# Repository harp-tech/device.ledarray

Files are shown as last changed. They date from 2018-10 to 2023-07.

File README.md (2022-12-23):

## Harp LED array

Controlling LED arrays that require more power. Ideally for opto-stimulation experiments.

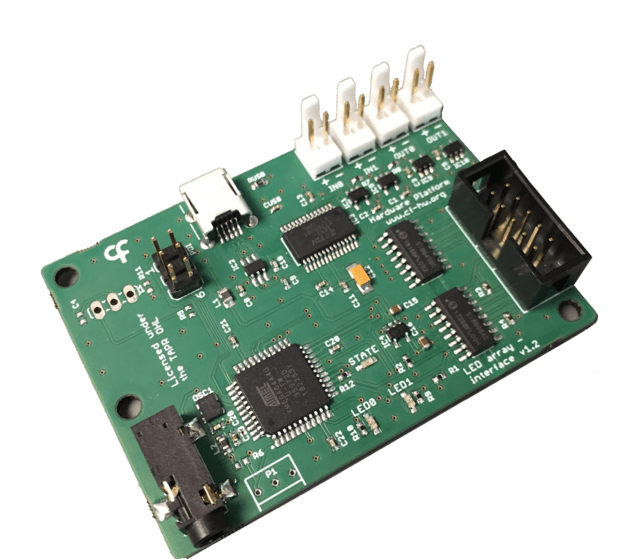
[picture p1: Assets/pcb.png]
harpledarray


### Key Features ###

* Controls up to 2 separate RGB LED
* Arrays and one common Infrared LED
* Two operation modes for each RGB LED Array: PWM or Interval

### Connectivity ###

* 1x clock sync input (CLKIN) [stereo jack]
* 1x USB (for computer) [USB type B]
* 1x flat cable
* 2x Digital Inputs (IN0, IN1) [flick lock male pins]
* 2x Digital Outputs (OUT0, OUT1) [flick lock male pins]
* 1x connector for 2 LED Arrays [10-pin flat-cable]

## Interface ##

The interface with the Harp board can be done through [Bonsai](https://bonsai-rx.org/) or a dedicated GUI (Graphical User Interface).

In order to use this GUI, there are some software that needs to be installed:

1 - Install the [drivers](https://bitbucket.org/fchampalimaud/downloads/downloads/UsbDriver-2.12.26.zip).

2 - Install the [runtime](https://bitbucket.org/fchampalimaud/downloads/downloads/Runtime-1.0.zip).

3 - Reboot the computer.

4 - Install the [GUI](https://bitbucket.org/fchampalimaud/downloads/downloads/Harp%20Led%20Array%20v2.2.0.zip).

## Licensing ##

Each subdirectory will contain a license or, possibly, a set of licenses if it involves both hardware and software.

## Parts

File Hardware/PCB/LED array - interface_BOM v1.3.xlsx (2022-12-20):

Part(s) | Quantity | Description | Distributor | Part. No.
IC1, IC5, IC9, IC10 | 4 | SINGLE BUS BUFFER GATE | Mouser | 595-SN74LVC1G125DBVR
IC2 | 1 | ESD Protection Low Cap | Mouser | 511-USBLC6-2SC6
IC3 | 1 | IC USB USB to Serial UART Enhanced IC SSOP-28 | Mouser | 895-FT232RL
IC4 | 1 | LP5907MFX-3.3/NOPB LDO 3.3Vout, 250mA | Mouser | 595-LP5907MFX-3.3NPB
IC6 | 1 | ATXMEGA64A4U-AU, ATxmega, 32 MHz, 64 KB, 4 KB, 44, TQFP | Mouser | 556-ATXMEGA64A4U-AU
IC7 | 1 | Isolator Si8645BC-B-IS1 | Mouser | 634-SI8645BC-B-IS1
IC8 | 1 | Isolator SI8606AC-B-IS1 | Mouser | 634-SI8606AC-B-IS1
L1 | 1 | MI0805K400R-10 FERRITE, BEAD, 2012, 100MHZ, 40R | Mouser | 875-MI0805K400R-10
L2 | 1 | FERRITE BEAD, 0.07OHM, 1.5A, 0603 | Mouser | 81-BLM18SG331TN1D
R9, R10, R12 | 3 | RES SMD 0402 68Ω, ± 5% | Mouser | 667-ERJ-2GEJ680X
R6 | 0 | RES SMD 0402 1kΩ, ± 0.1% | Farnell | 1697320
R1, R2, R3, R4 | 4 | RES SMD 0402 3kΩ, ± 1% | Mouser | 667-ERJ-2RKF3001X
R7, R8 | 2 | RES SMD 0402 100kΩ, ± 1% | REEL | REEL
RUSB | 1 | RES SMD 1MΩ 1/4W 5% 75V 0603 | Mouser | 71-CRCW06031M00JNEAH
C9, C10 | 2 | CAP CER 47pF 50V C0G 5% 0402 | Mouser | 81-GCM1555C1H470JA6D
CUSB | 1 | CAP CER 4.7nF 50 V ± 10% 0402 | Mouser | 710-885012205048
C1, C2, C3, C5, C8, C11, C13, C14, C20, C21, C22, C28 | 11 | CAP CER 100nF 10V X5R 0402 | REEL | REEL
C23 | 1 | CAP CER 0.33uF 16V 10% X72 0402 | Mouser | 810-CGA2B1X7S1C334KC
C15, C16 | 2 | CAP CER 4.7uF 35V X5R 10% 0603 | Mouser | 81-GRM188R6YA475KE5D
C12 | 1 | CAP TAN 4.7uF 10V 10% | Mouser | 80-T494A475M010
LED0, LED1, STATE | 3 | LED, Green, 1.6mm x 0.8mm, 566 nm, 2.1 V, 20 mA, 15 mcd | Mouser | 78-TLMP1100-GS08
P1 | 0 | SQ 500 OHM 10% 0.5WATTS | Mouser | 652-3362M-1-501LF
JP1 | 1 | 10 Contacts, Header, 2.54 mm, Through Hole, 2 Rows | Mouser | 517-30310-6002
USB | 1 | USB MINI B RECEPT RA TH W/POST | Mouser | 798-UX60-MB-5S8
USB Cable | 1 | USB A - MINI-B 0.8M - MINI-B 0.8M BLACK | Mouser | 538-88732-8502
OSC1 | 1 | 32MHz 10ppm | Mouser | 998-1001CI5032.0000T
CLKIN | 1 | SMT 3.5 STEREO REEL | Mouser | 502-35RASMT2BHNTRX
PDI | 1 | CONN HEADER 6POS .100 STR | Mouser | 649-67996-206HLF
IN0, IN1, OUT0, OUT1 | 4 | Vertical, KK 6410 Series, 2 Contacts, Header, 2.54 mm | Mouser | 538-22-29-2021
SV1 | 0 | 3POS Gold Male | Mouser | 649-68001-203HLF
Components | 53
Licensed under the TAPR Open Hardware License (www.tapr.org/OHL)
Copyright 2018 Artur Silva and Filipe Carvalho

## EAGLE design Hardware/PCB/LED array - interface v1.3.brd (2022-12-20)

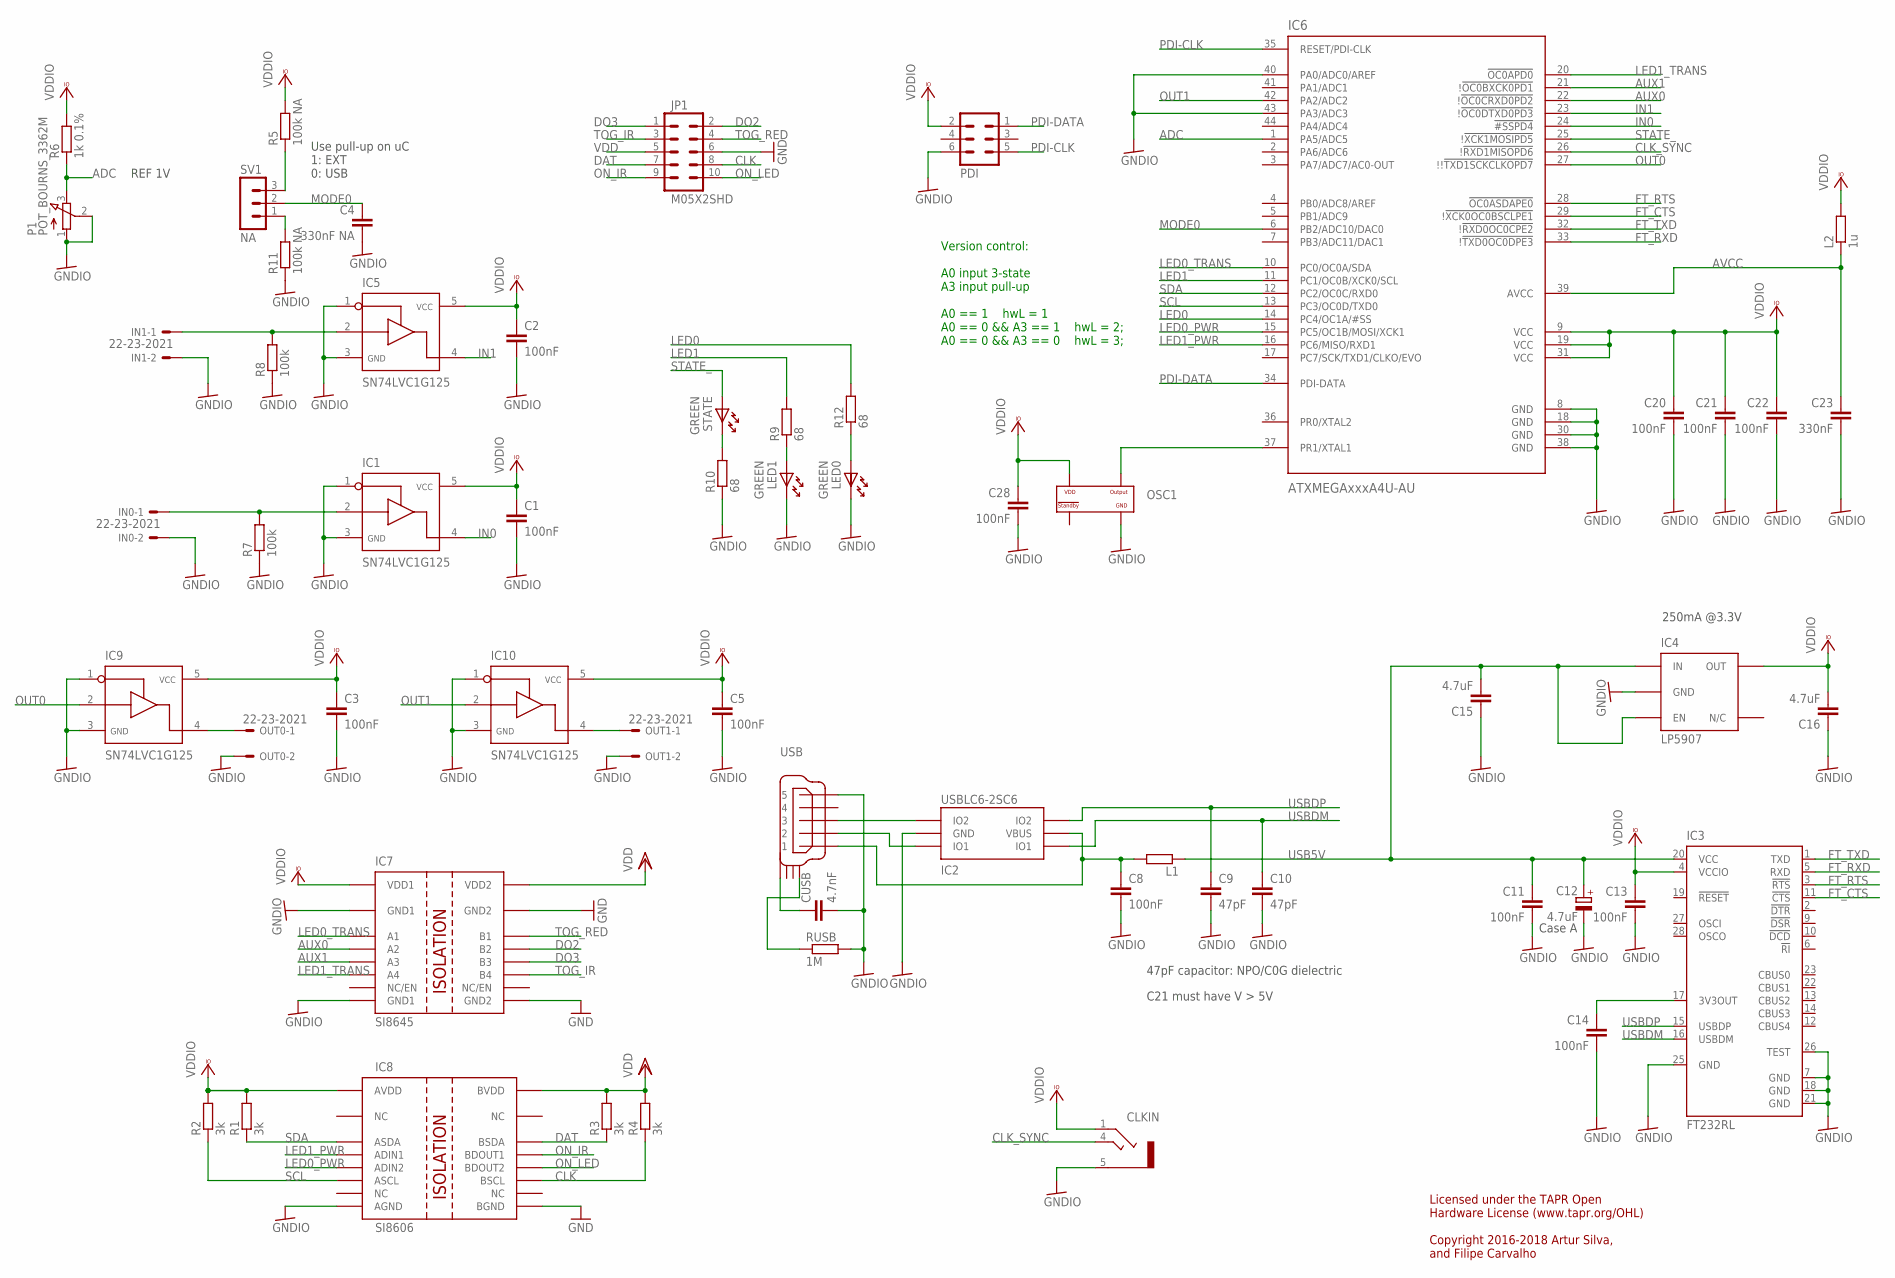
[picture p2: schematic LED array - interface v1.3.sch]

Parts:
C1, C2, C3, C5, C8, C11, C13, C14, C20, C21, C22, C28: 100nF; C0402
C4: 330nF NA; C0402
C9, C10: 47pF; C0402
C12: 4.7uF; A/3216-18W
C15, C16: 4.7uF; C0402
C23: 330nF; C0402
CLKIN: STEREO_JACK; 35RASMT2BHNTRX
CUSB: 4.7nF; C0402
IC1, IC5, IC9, IC10: SN74LVC1G125; SOT23-5
IC2: USBLC6-2SC6; SOT23-6L
IC3: FT232RL; SSOP28
IC4: LP5907; TSOT23-5
IC6: ATXMEGAxxxA4U-AU; QFP80P1200X1200X120-44N
IC7: SI8645; NSOIC-16
IC8: SI8606; NSOIC-16
IN0, IN1: 22-23-2021
JP1: M05X2SHD; 2X5-SHROUDED
L1: ???; R0805
L2: 1u; R0805
LED0, LED1: GREEN; LED_HAND
OSC1: OSCILLATOR; OSCILLATOR_3.2X2.5
OUT0, OUT1: 22-23-2021
P1: POT_BOURNS_3362M
PDI: MA03-2
R1, R2, R3, R4: 3k; R0402
R5, R11: 100k NA; R0402
R6: 1k 0.1%; R0402
R7, R8: 100k; R0402
R9, R10, R12: 68; R0402
RUSB: 1M; R0603
STATE: GREEN; LED_HAND
SV1: NA; MA03-1
USB: USB_MINI_B; 240-0002-1

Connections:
ADC: IC6.1 (PA5/ADC5), P1.3 (E), R6.1
ADC1: R5.1, SV1.3
AUX0: IC6.22 (!!OC0CRXD0PD2), IC7.4 (A2)
AUX1: IC6.21 (!!OC0BXCK0PD1), IC7.5 (A3)
AVCC: C23.1, IC6.39 (AVCC), L2.1
CLK: IC8.11 (BSCL), JP1.8, R4.1
CLK_SYNC: CLKIN.4, IC6.26 (!!RXD1MISOPD6)
DAT: IC8.14 (BSDA), JP1.7, R3.1
DO2: IC7.13 (B2), JP1.2
DO3: IC7.12 (B3), JP1.1
FT_CTS: IC3.11 (!CTS), IC6.29 (!!XCK0OC0BSCLPE1)
FT_RTS: IC3.3 (!RTS), IC6.28 (!OC0ASDAPE0)
FT_RXD: IC3.5 (RXD), IC6.33 (!!TXD0OC0DPE3)
FT_TXD: IC3.1 (TXD), IC6.32 (!!RXD0OC0CPE2)
GND: IC7.9 (GND2), IC7.15 (GND2), IC8.9 (BGND), JP1.6
GND2: IC5.2, IN1.1, R8.2
GNDIO: C1.2, C2.2, C3.2, C4.2, C5.2, C8.2, C9.2, C10.2, C11.2, C12.-, C13.2, C14.2, C15.1, C16.1, C20.2, C21.2, C22.2, C23.2, C28.2, CLKIN.5, CUSB.2, IC1.1, IC1.3, IC2.P$2 (GND), IC3.7 (GND), IC3.18 (GND), IC3.21 (GND), IC3.25 (GND), IC3.26 (TEST), IC4.2 (GND), IC5.1, IC5.3, IC6.8 (GND), IC6.18 (GND), IC6.30 (GND), IC6.38 (GND), IC6.40 (PA0/ADC0/AREF), IC6.43 (PA3/ADC3), IC7.2 (GND1), IC7.8 (GND1), IC8.8 (AGND), IC9.1, IC9.3, IC10.1, IC10.3, IN0.2, IN1.2, LED0.K, LED1.K, OSC1.P$2 (GND), OUT0.2, OUT1.2, P1.1 (A), P1.2 (S), PDI.6, R7.1, R8.1, R10.1, R11.1, RUSB.2, USB.P$5 (5)
IN0: IC1.4, IC6.24 (!#SSPD4)
IN1: IC5.4, IC6.23 (!!OC0DTXD0PD3)
LED0: IC6.14 (PC4/OC1A/#SS), R12.2
LED0_PWR: IC6.15 (PC5/OC1B/MOSI/XCK1), IC8.5 (ADIN2)
LED0_TRANS: IC6.10 (PC0/OC0A/SDA), IC7.3 (A1)
LED1: IC6.11 (PC1/OC0B/XCK0/SCL), R9.2
LED1_PWR: IC6.16 (PC6/MISO/RXD1), IC8.4 (ADIN1)
LED1_TRANS: IC6.20 (!OC0APD0), IC7.6 (A4)
MODE0: C4.1, IC6.6 (PB2/ADC10/DAC0), SV1.2
unnamed: R11.2, SV1.1
unnamed: C14.1, IC3.17 (3V3OUT)
unnamed: IC9.4, OUT0.1
unnamed: IC2.P$3 (IO2), USB.P$3 (3)
unnamed: LED0.A, R12.1
unnamed: IC10.4, OUT1.1
unnamed: R10.2, STATE.K
unnamed: IC1.2, IN0.1, R7.2
unnamed: LED1.A, R9.1
unnamed: C8.1, IC2.P$5 (VBUS), L1.2, USB.P$1 (1)
unnamed: IC2.P$1 (IO1), USB.P$2 (2)
unnamed: CUSB.1, USB.SHIELD_4
unnamed: RUSB.1, USB.SHIELD_1
ON_IR: IC8.13 (BDOUT1), JP1.9
ON_LED: IC8.12 (BDOUT2), JP1.10
OSC1: IC6.37 (PR1/XTAL1), OSC1.P$3 (OUTPUT)
OUT0: IC6.27 (!!!TXD1SCKCLKOPD7), IC9.2
OUT1: IC6.42 (PA2/ADC2), IC10.2
PDI-CLK: IC6.35 (RESET/PDI-CLK), PDI.5
PDI-DATA: IC6.34 (PDI-DATA), PDI.1
SCL: IC6.13 (PC3/OC0D/TXD0), IC8.6 (ASCL), R2.1
SDA: IC6.12 (PC2/OC0C/RXD0), IC8.3 (ASDA), R1.1
STATE_: IC6.25 (!!XCK1MOSIPD5), STATE.A
TOG_IR: IC7.11 (B4), JP1.3
TOG_RED: IC7.14 (B1), JP1.4
USB5V: C11.1, C12.+, C15.2, IC3.20 (VCC), IC4.1 (IN), IC4.3 (EN), L1.1
USBDM: C10.1, IC2.P$6 (IO1), IC3.16 (USBDM)
USBDP: C9.1, IC2.P$4 (IO2), IC3.15 (USBDP)
VCCIO: C1.1, C2.1, C3.1, C5.1, C13.1, C16.2, C20.1, C21.1, C22.1, C28.1, CLKIN.1, IC1.5, IC3.4 (VCCIO), IC4.5 (OUT), IC5.5, IC6.9 (VCC), IC6.19 (VCC), IC6.31 (VCC), IC7.1 (VDD1), IC8.1 (AVDD), IC9.5, IC10.5, L2.2, OSC1.P$4 (VDD), PDI.2, R1.2, R2.2, R5.2, R6.2
VDD: IC7.16 (VDD2), IC8.16 (BVDD), JP1.5, R3.2, R4.2

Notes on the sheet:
250mA @3.3V
Case A
47pF capacitor: NPO/C0G dielectric
C21 must have V > 5V
Use pull-up on uC 1: EXT 0: USB
REF 1V
Licensed under the TAPR Open Hardware License (www.tapr.org/OHL) Copyright 2016-2018 Artur Silva, and Filipe Carvalho
Version control: A0 input 3-state A3 input pull-up A0 == 1 hwL = 1 A0 == 0 && A3 == 1 hwL = 2; A0 == 0 && A3 == 0 hwL = 3;

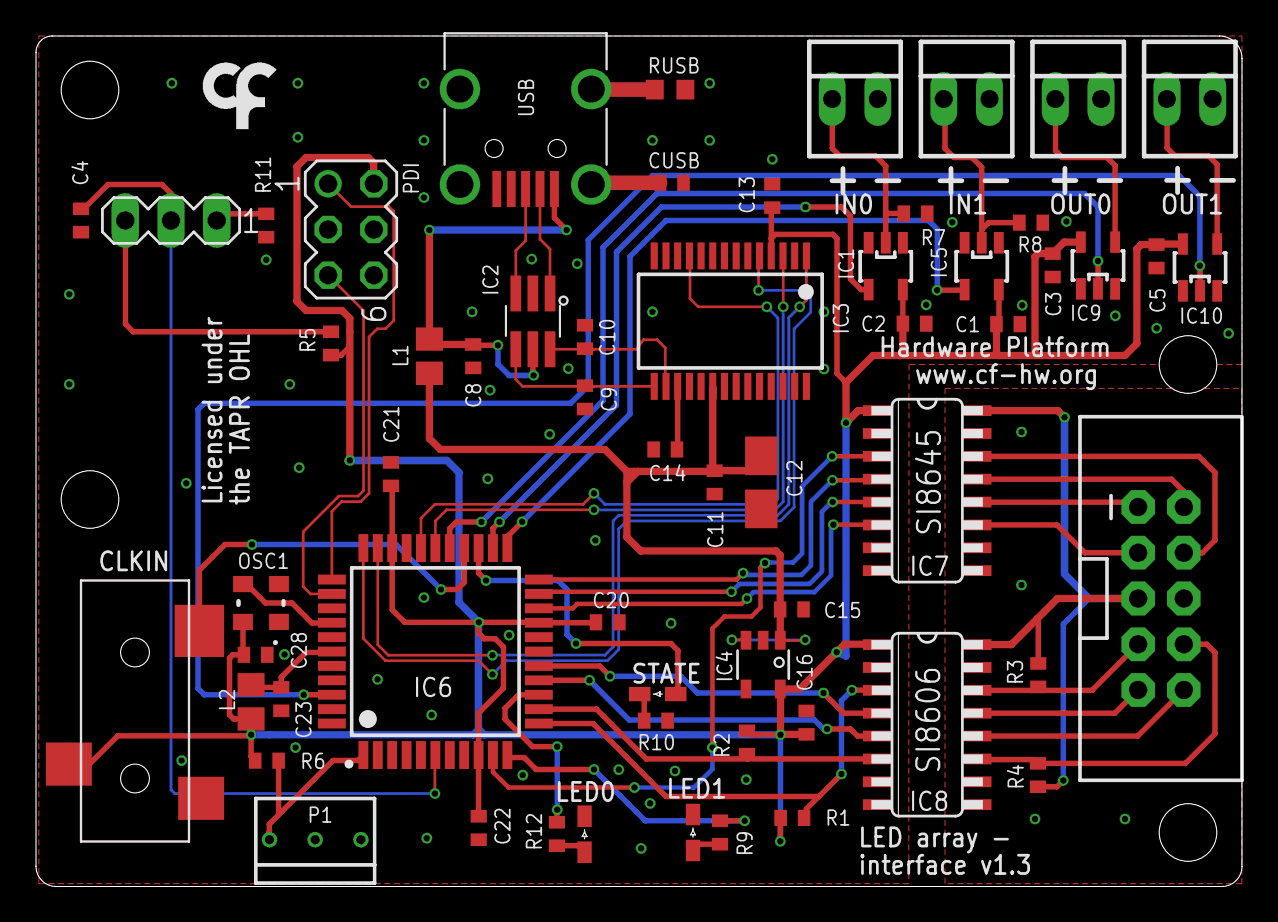
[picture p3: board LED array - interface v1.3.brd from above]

Board: 2 copper layers, 67.0 x 47.2 mm, 61 parts (1 on the bottom side), 56 nets.

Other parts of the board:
U$1: LOGO_5
U$3: LOGO_7

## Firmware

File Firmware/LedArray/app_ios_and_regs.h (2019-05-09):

#ifndef _APP_IOS_AND_REGS_H_
#define _APP_IOS_AND_REGS_H_
#include "cpu.h"

void init_ios(void);
/************************************************************************/
/* Definition of input pins                                             */
/************************************************************************/
// VERSION0               Description: Check hardware version
// VERSION1               Description: Check hardware version
// IN0                    Description: Board's input IN0
// IN1                    Description: Board's input IN1

#define read_VERSION0 read_io(PORTA, 0)         // VERSION0
#define read_VERSION1 read_io(PORTA, 3)         // VERSION1
#define read_IN0 read_io(PORTD, 4)              // IN0
#define read_IN1 read_io(PORTD, 3)              // IN1

/************************************************************************/
/* Definition of output pins                                            */
/************************************************************************/
// LED0_TRANSISTOR        Description: Controls transistor of LED0
// BOARD_LED1             Description: Board's LED1
// LED0_PWR_ON            Description: Enables power for LED0
// LED1_PWR_ON            Description: Enables power for LED1
// LED1_TRANSISTOR        Description: Controls transistor of LED1
// AUX1                   Description: Dummy digital output
// AUX0                   Description: Dummy digital output
// BOARD_LED0             Description: Board's LED0
// OUT0                   Description: Board's output OUT1
// OUT1                   Description: Board's output OUT0

/* LED0_TRANSISTOR */
#define set_LED0_TRANSISTOR set_io(PORTC, 0)
#define clr_LED0_TRANSISTOR clear_io(PORTC, 0)
#define tgl_LED0_TRANSISTOR toggle_io(PORTC, 0)
#define read_LED0_TRANSISTOR read_io(PORTC, 0)

/* BOARD_LED1 */
#define set_BOARD_LED1 set_io(PORTC, 1)
#define clr_BOARD_LED1 clear_io(PORTC, 1)
#define tgl_BOARD_LED1 toggle_io(PORTC, 1)
#define read_BOARD_LED1 read_io(PORTC, 1)

/* LED0_PWR_ON */
#define set_LED0_PWR_ON set_io(PORTC, 5)
#define clr_LED0_PWR_ON clear_io(PORTC, 5)
#define tgl_LED0_PWR_ON toggle_io(PORTC, 5)
#define read_LED0_PWR_ON read_io(PORTC, 5)

/* LED1_PWR_ON */
#define set_LED1_PWR_ON set_io(PORTC, 6)
#define clr_LED1_PWR_ON clear_io(PORTC, 6)
#define tgl_LED1_PWR_ON toggle_io(PORTC, 6)
#define read_LED1_PWR_ON read_io(PORTC, 6)

/* LED1_TRANSISTOR */
#define set_LED1_TRANSISTOR set_io(PORTD, 0)
#define clr_LED1_TRANSISTOR clear_io(PORTD, 0)
#define tgl_LED1_TRANSISTOR toggle_io(PORTD, 0)
#define read_LED1_TRANSISTOR read_io(PORTD, 0)

/* AUX1 */
#define set_AUX1 set_io(PORTD, 1)
#define clr_AUX1 clear_io(PORTD, 1)
#define tgl_AUX1 toggle_io(PORTD, 1)
#define read_AUX1 read_io(PORTD, 1)

/* AUX0 */
#define set_AUX0 set_io(PORTD, 2)
#define clr_AUX0 clear_io(PORTD, 2)
#define tgl_AUX0 toggle_io(PORTD, 2)
#define read_AUX0 read_io(PORTD, 2)

/* BOARD_LED0 */
#define set_BOARD_LED0 set_io(PORTC, 4)
#define clr_BOARD_LED0 clear_io(PORTC, 4)
#define tgl_BOARD_LED0 toggle_io(PORTC, 4)
#define read_BOARD_LED0 read_io(PORTC, 4)

/* OUT0 */
#define set_OUT0 set_io(PORTD, 7)
#define clr_OUT0 clear_io(PORTD, 7)
#define tgl_OUT0 toggle_io(PORTD, 7)
#define read_OUT0 read_io(PORTD, 7)

/* OUT1 */
#define set_OUT1 set_io(PORTA, 2)
#define clr_OUT1 clear_io(PORTA, 2)
#define tgl_OUT1 toggle_io(PORTA, 2)
#define read_OUT1 read_io(PORTA, 2)


/************************************************************************/
/* Registers' structure                                                 */
/************************************************************************/
typedef struct
{
	uint8_t REG_POWER_EN;
	uint8_t REG_LED_BEHAVING;
	uint8_t REG_LED_ON;
	uint8_t REG_IN_STATE;
	uint8_t REG_OUT_CONFIGURATION;
	uint8_t REG_IN_CONFIGURATION;
	uint8_t REG_LED_CONFIGURATION;
	uint8_t REG_LED0_SUPPLY_PWR_CONF;
	uint8_t REG_LED1_SUPPLY_PWR_CONF;
	float REG_LED0_PWM_FREQ;
	float REG_LED0_PWM_DCYCLE;
	uint16_t REG_LED0_PWM_PULSES;
	uint16_t REG_LED0_INTERVAL_ON;
	uint16_t REG_LED0_INTERVAL_OFF;
	uint16_t REG_LED0_INTERVAL_PULSES;
	uint16_t REG_LED0_INTERVAL_TAIL;
	uint16_t REG_LED0_INTERVAL_REPS;
	float REG_LED1_PWM_FREQ;
	float REG_LED1_PWM_DCYCLE;
	uint16_t REG_LED1_PWM_PULSES;
	uint16_t REG_LED1_INTERVAL_ON;
	uint16_t REG_LED1_INTERVAL_OFF;
	uint16_t REG_LED1_INTERVAL_PULSES;
	uint16_t REG_LED1_INTERVAL_TAIL;
	uint16_t REG_LED1_INTERVAL_REPS;
	float REG_LED0_PWM_FREQ_REAL;
	float REG_LED0_PWM_DCYCLE_REAL;
	float REG_LED1_PWM_FREQ_REAL;
	float REG_LED1_PWM_DCYCLE_REAL;
	uint8_t REG_AUX_DIG_OUT;
	uint8_t REG_AUX_SUPPLY_PWR_CONF;
	uint8_t REG_OUT_STATE;
	uint8_t REG_DUMMY0;
	uint8_t REG_EVNT_ENABLE;
} AppRegs;

/************************************************************************/
/* Registers' address                                                   */
/************************************************************************/
/* Registers */
#define ADD_REG_POWER_EN                    32 // U8     Control the enable of both LEDs' supply
#define ADD_REG_LED_BEHAVING                33 // U8     Starts and stops the LED is behaving
#define ADD_REG_LED_ON                      34 // U8     Controls the on board's LED
#define ADD_REG_IN_STATE                    35 // U8     Reflects the state of both inputs
#define ADD_REG_OUT_CONFIGURATION           36 // U8     Configures which signal is connected to the digital outputs
#define ADD_REG_IN_CONFIGURATION            37 // U8     Configures the digital inputs
#define ADD_REG_LED_CONFIGURATION           38 // U8     Configures how LEDs will behave
#define ADD_REG_LED0_SUPPLY_PWR_CONF        39 // U8     Configuration of power to be aplied to LED0 [1;120]
#define ADD_REG_LED1_SUPPLY_PWR_CONF        40 // U8     Configuration of power to be aplied to LED1 [1;120]
#define ADD_REG_LED0_PWM_FREQ               41 // FLOAT  PWM frequency of LED0's power transistor [0.5;2000.0]
#define ADD_REG_LED0_PWM_DCYCLE             42 // FLOAT  PWM duty cycle of LED0's power transistor [0.1;99.9]
#define ADD_REG_LED0_PWM_PULSES             43 // U16    Number of PWM pulses (LED0) [1;65535]
#define ADD_REG_LED0_INTERVAL_ON            44 // U16    Time ON of LED0 (milliseconds) [1;65535]
#define ADD_REG_LED0_INTERVAL_OFF           45 // U16    Time OFF of LED0 (milliseconds) [1;65535]
#define ADD_REG_LED0_INTERVAL_PULSES        46 // U16    Number of pulses (LED0) [1;65535]
#define ADD_REG_LED0_INTERVAL_TAIL          47 // U16    Wait time between pulses (milliseconds) (LED0) [1;65535]
#define ADD_REG_LED0_INTERVAL_REPS          48 // U16    Number of repetitions of the entire scheme (LED0) [1;65535]
#define ADD_REG_LED1_PWM_FREQ               49 // FLOAT  PWM frequency of LED1's power transistor [0.5;2000.0]
#define ADD_REG_LED1_PWM_DCYCLE             50 // FLOAT  PWM duty cycle of LED1's power transistor [0.1;99.9]
#define ADD_REG_LED1_PWM_PULSES             51 // U16    Number of PWM pulses (LED1) [1;65535]
#define ADD_REG_LED1_INTERVAL_ON            52 // U16    Time ON of LED1 (milliseconds) [1;65535]
#define ADD_REG_LED1_INTERVAL_OFF           53 // U16    Time OFF of LED1 (milliseconds) [1;65535]
#define ADD_REG_LED1_INTERVAL_PULSES        54 // U16    Number of pulses (LED1) [1;65535]
#define ADD_REG_LED1_INTERVAL_TAIL          55 // U16    Wait time between pulses (milliseconds) (LED1) [1;65535]
#define ADD_REG_LED1_INTERVAL_REPS          56 // U16    Number of repetitions of the entire scheme (LED1) [1;65535]
#define ADD_REG_LED0_PWM_FREQ_REAL          57 // FLOAT  Real PWM frequency of LED0's power transistor
#define ADD_REG_LED0_PWM_DCYCLE_REAL        58 // FLOAT  Real PWM duty cycle of LED0's power transistor
#define ADD_REG_LED1_PWM_FREQ_REAL          59 // FLOAT  Real PWM frequency of LED1's power transistor
#define ADD_REG_LED1_PWM_DCYCLE_REAL        60 // FLOAT  Real PWM duty cycle of LED1's power transistor
#define ADD_REG_AUX_DIG_OUT                 61 // U8     Controls the auxiliar digital output
#define ADD_REG_AUX_SUPPLY_PWR_CONF         62 // U8     Configuration of power to be aplied to auxiliar LED [1;120]
#define ADD_REG_OUT_STATE                   63 // U8     Digital output control
#define ADD_REG_DUMMY0                      64 // U8     Not used
#define ADD_REG_EVNT_ENABLE                 65 // U8     Enable the Events

/************************************************************************/
/* PWM Generator registers' memory limits                               */
/*                                                                      */
/* DON'T change the APP_REGS_ADD_MIN value !!!                          */
/* DON'T change these names !!!                                         */
/************************************************************************/
/* Memory limits */
#define APP_REGS_ADD_MIN                    0x20
#define APP_REGS_ADD_MAX                    0x41
#define APP_NBYTES_OF_REG_BANK              70
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

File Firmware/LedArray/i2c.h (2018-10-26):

#ifndef _I2C_H_
#define _I2C_H_

#include "i2c_user.h"


//*****************************************************************************
// If not defined, define bool, true and false
//*****************************************************************************
#ifndef bool
	#define bool uint8_t
#endif
#ifndef true
	#define true 1
#endif
#ifndef false
	#define false 0
#endif

//*****************************************************************************
// Define I2C structure for the devices
//*****************************************************************************
#ifndef MAX_I2C_DATA
	#define MAX_I2C_DATA 32
#endif

typedef struct {
	unsigned char add;
	unsigned char reg;
	unsigned char reg_val;
	unsigned char data[MAX_I2C_DATA];
} i2c_dev_t;


//*****************************************************************************
// Check if any of the four I2C buses is used
//*****************************************************************************
#ifdef I2C0_CLK
	#ifndef I2C0_PORT
		#error "Bus I2C0 is enabled but I2C0_PORT is not defined"
	#endif
	#ifndef I2C0_SDA
		#error "Bus I2C0 is enabled but I2C0_SDA is not defined"
	#endif
	#ifndef I2C0_SCL
		#error "Bus I2C0 is enabled but I2C0_SCL is not defined"
	#endif
	#ifndef F_CPU
		#error "Bus I2C0 is enabled but F_CPU is not defined"
	#endif
	#if   F_CPU == 32000000
	#elif F_CPU == 16000000
	#elif F_CPU ==  8000000
	#elif F_CPU ==  4000000
	#elif F_CPU ==  2000000
	#elif F_CPU ==  1000000
	#else
	#error "I2C0: Unsupported F_CPU value for system clock"
	#endif
#endif

#ifdef I2C1_CLK
	#ifndef I2C1_PORT
		#error "Bus I2C1 is enabled but I2C1_PORT is not defined"
	#endif
	#ifndef I2C1_SDA
		#error "Bus I2C1 is enabled but I2C1_SDA is not defined"
	#endif
	#ifndef I2C1_SCL
		#error "Bus I2C1 is enabled but I2C1_SCL is not defined"
	#endif
	#ifndef F_CPU
		#error "Bus I2C1 is enabled but F_CPU is not defined"
	#endif
	#if   F_CPU == 32000000
	#elif F_CPU == 16000000
	#elif F_CPU ==  8000000
	#elif F_CPU ==  4000000
	#elif F_CPU ==  2000000
	#elif F_CPU ==  1000000
	#else
	#error "I2C1: Unsupported F_CPU value for system clock"
	#endif
#endif

#ifdef I2C2_CLK
	#ifndef I2C2_PORT
		#error "Bus I2C2 is enabled but I2C2_PORT is not defined"
	#endif
	#ifndef I2C2_SDA
		#error "Bus I2C2 is enabled but I2C2_SDA is not defined"
	#endif
	#ifndef I2C2_SCL
		#error "Bus I2C2 is enabled but I2C2_SCL is not defined"
	#endif
	#ifndef F_CPU
		#error "Bus I2C2 is enabled but F_CPU is not defined"
	#endif
	#if   F_CPU == 32000000
	#elif F_CPU == 16000000
	#elif F_CPU ==  8000000
	#elif F_CPU ==  4000000
	#elif F_CPU ==  2000000
	#elif F_CPU ==  1000000
	#else
	#error "I2C2: Unsupported F_CPU value for system clock"
	#endif
#endif

#ifdef I2C3_CLK
	#ifndef I2C3_PORT
		#error "Bus I2C3 is enabled but I2C3_PORT is not defined"
	#endif
	#ifndef I2C3_SDA
		#error "Bus I2C3 is enabled but I2C3_SDA is not defined"
	#endif
	#ifndef I2C3_SCL
		#error "Bus I2C3 is enabled but I2C3_SCL is not defined"
	#endif
	#ifndef F_CPU
		#error "Bus I2C3 is enabled but F_CPU is not defined"
	#endif
	#if   F_CPU == 32000000
	#elif F_CPU == 16000000
	#elif F_CPU ==  8000000
	#elif F_CPU ==  4000000
	#elif F_CPU ==  2000000
	#elif F_CPU ==  1000000
	#else
	#error "I2C3: Unsupported F_CPU value for system clock"
	#endif
#endif



//*****************************************************************************
// Define SCL delays
//*****************************************************************************
#ifdef I2C0_CLK
	#define tCLK_I2C0 I2C0_CLK
#endif
#ifdef I2C1_CLK
	#define tCLK_I2C1 I2C1_CLK
#endif
#ifdef I2C2_CLK
	#define tCLK_I2C2 I2C2_CLK
#endif
#ifdef I2C3_CLK
	#define tCLK_I2C3 I2C3_CLK
#endif

//*****************************************************************************
// Define IOs interface
//*****************************************************************************
#ifdef I2C0_CLK
	#define set_SDA0 set_io(I2C0_PORT, I2C0_SDA)
	#define clear_SDA0 clear_io(I2C0_PORT, I2C0_SDA)
	#define toggle_SDA0 toggle_io(I2C0_PORT, I2C0_SDA)
	#define set_SCL0 set_io(I2C0_PORT, I2C0_SCL)
	#define clear_SCL0 clear_io(I2C0_PORT, I2C0_SCL)
	#define toggle_SCL0 toggle_io(I2C0_PORT, I2C0_SCL)
	#define read_SDA0 read_io(I2C0_PORT, I2C0_SDA)
	#define set_SDA0_and_SCL0 set_io_mask(I2C0_PORT, (1<<I2C0_SDA) | (1<<I2C0_SCL))
	#define clear_SDA0_and_SCL0 clear_io_mask(I2C0_PORT, (1<<I2C0_SDA) | (1<<I2C0_SCL))
#endif

#ifdef I2C1_CLK
	#define set_SDA1 set_io(I2C1_PORT, I2C1_SDA)
	#define clear_SDA1 clear_io(I2C1_PORT, I2C1_SDA)
	#define toggle_SDA1 toggle_io(I2C1_PORT, I2C1_SDA)
	#define set_SCL1 set_io(I2C1_PORT, I2C1_SCL)
	#define clear_SCL1 clear_io(I2C1_PORT, I2C1_SCL)
	#define toggle_SCL1 toggle_io(I2C1_PORT, I2C1_SCL)
	#define read_SDA1 read_io(I2C1_PORT, I2C1_SDA)
	#define set_SDA1_and_SCL1 set_io_mask(I2C1_PORT, (1<<I2C1_SDA) | (1<<I2C1_SCL))
	#define clear_SDA1_and_SCL1 clear_io_mask(I2C1_PORT, (1<<I2C1_SDA) | (1<<I2C1_SCL))
#endif

#ifdef I2C2_CLK
	#define set_SDA2 set_io(I2C2_PORT, I2C2_SDA)
	#define clear_SDA2 clear_io(I2C2_PORT, I2C2_SDA)
	#define toggle_SDA2 toogle_io(I2C2_PORT, I2C2_SDA)
	#define set_SCL2 set_io(I2C2_PORT, I2C2_SCL)
	#define clear_SCL2 clear_io(I2C2_PORT, I2C2_SCL)
	#define toggle_SCL2 toogle_io(I2C2_PORT, I2C2_SCL)
	#define read_SDA2 read_io(I2C2_PORT, I2C2_SDA)
	#define set_SDA2_and_SCL2 set_io_mask(I2C2_PORT, (1<<I2C2_SDA) | (1<<I2C2_SCL))
	#define clear_SDA2_and_SCL2 clear_io_mask(I2C2_PORT, (1<<I2C2_SDA) | (1<<I2C2_SCL))
#endif

#ifdef I2C3_CLK
	#define set_SDA3 set_io(I2C3_PORT, I2C3_SDA)
	#define clear_SDA3 clear_io(I2C3_PORT, I2C3_SDA)
	#define toggle_SDA3 toogle_io(I2C3_PORT, I2C3_SDA)
	#define set_SCL3 set_io(I2C3_PORT, I2C3_SCL)
	#define clear_SCL3 clear_io(I2C3_PORT, I2C3_SCL)
	#define toggle_SCL3 toogle_io(I2C3_PORT, I2C3_SCL)
	#define read_SDA3 read_io(I2C3_PORT, I2C3_SDA)
	#define set_SDA3_and_SCL3 set_io_mask(I2C3_PORT, (1<<I2C3_SDA) | (1<<I2C3_SCL))
	#define clear_SDA3_and_SCL3 clear_io_mask(I2C3_PORT, (1<<I2C3_SDA) | (1<<I2C3_SCL))
#endif
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

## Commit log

2018-10-26 Added the firmware files.
    [registers.xls]
2018-10-30 Added new registers and renamed some digital lines.
    [registers.xls]
2019-05-09 Implemented control of the digtal outputs.
    [registers.xls]
2019-08-09 Ability to turn LED's transistor off when stop the behavior. Increased version to fw 2.3.
2022-12-20 Add PCB and BOM files
    [LED array - interface v1.3.brd, LED array - interface v1.3.sch, LED array - interface_BOM v1.3.xlsx]
2022-12-23 refactor repository structure
    [LED array - interface v1.3.brd, LED array - interface v1.3.sch, LED array - interface_BOM v1.3.xlsx]
2023-07-06 update pcb asset image
2023-07-24 update device.yml with new LED modes naming
2023-07-26 Align .gitignore to other device repositories
2023-07-26 Regenerate device classes
2024-11-13 Update device schema source

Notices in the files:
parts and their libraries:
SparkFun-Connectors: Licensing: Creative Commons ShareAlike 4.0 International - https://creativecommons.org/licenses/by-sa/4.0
